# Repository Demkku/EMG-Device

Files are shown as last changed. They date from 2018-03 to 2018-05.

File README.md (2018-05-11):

Everything done, everything up to date and project presented.

final presentation:
https://docs.google.com/presentation/d/1xxOuLbYDE3mbfAP0H2NyMZXC_jU_autwXX0Ozza_mss/edit?usp=sharing

repository:
https://github.com/Demkku/EMG-Device

diary:
https://demkku.github.io/EMG-Device/

## Summary report

click [here]({{ site.baseurl }}/assets/EMG summary report.pdf) to download the summary report PDF with pictures and links
Note! link only available when browsing github pages and the link doesn't seem to work with Edge Browser

Our final concept was to measure heart rate using voltage sensors that have been amplified and filtered using operational amplifiers. Then the heart rate peak is detected with Arduino and the time difference between the peaks is measured and converted for a servo. Then the servo moves a needle on a measuring table to display the heart rate.

Our project consists of 4 elements: a circuit board and a case for it, a measuring table and software to read sensor data and convert into readable data and software to control a servo for the measuring table. 

Johannes designed the circuit board using KiCad. Voltage -sensors didn’t have strong enough signal, so in order to use it properly the signal had to be amplified and filtered using operational amplifiers. The voltage difference in the order of 1mV is measured across the chest with EKG electrodes, +, - and ground. The signal to an instrumental operational amplifier, where common mode noise is rejected, and the signal is amplified. Next, the signal goes through low and high pass filters. After filtering is further amplification and full wave rectification. Last, one more amplifier and then the signal goes to the ADC of ATMEGA328p. 

The case was designed by using Blender. Blender isn’t quite the best software in designing real life objects, but to create a simple and aesthetically nice case wasn’t a problem. The case was designed around the project images exported from Kicad. Some approximation by eye had to be made with components and they were pretty much correct. Only the size of the PCB would have gone terribly wrong if only the Kicad images were followed. The case was finally printed with Fortus 380mc printer. The result was fair, only the bottom was so thin that it cracked a little.

The measuring table was designed with Blender, from which the vector file was imported to Inkscape.
From Inkscape the vector file was exported as a pdf and then printed using a laser cutter out of plywood. The first cut table was too thick, and the servo couldn’t be put through. The arrow needed a hole for the screw, too. That’s why the table was cut again, and it turned out without problems. The servo was glued on the backside of the table.

The software was done on Arduino IDE platform. We programmed our code to ATMEGA328p microcontroller using Arduino UNO. The programs purpose was to measure the time difference between every heartbeat and calculate how many times the heart beats in a minute. EKG -sensors had a triangle wave that measured voltage of the heartbeat and it had some noise in it. To get reliable data we had to calculate the time difference between every peak of the voltage signal and not take the noise into account. We made the program to measure only the rising side of the wave and its maximum voltage. That way we got the most reliable data. Then we had to program a correct angle to a servo to display the heartrate on a measuring table.

Lessons learned 

We learned a lot in this project. We learned to use different software like KiCad, Blender, GitHub and Inkscape. We learned that one should always make a second version of the hardware design if any problems would rise. We learned how to use operational amplifiers in practice and how to compare different components to get the best one for its use. We also learned to watch carefully that everything gets correctly imported other software like all of our parts in the circuit board design didn’t get correctly imported to the drilling machine because we used KiCad as our design system.

We learned a good lesson in time management. It would be a lot better to divide the work of the project to entire period so there wouldn’t be such a rush at the end of the period to get everything done.

Our recommendation to others doing the same project is to take your time designing every element of the project carefully so everything goes smoothly when you start building up the project. This project can be a bit difficult so it would be better done in your on pace and not in an introductory course like Principles of digital fabrication.

Feedback to course responsibles

 The course was nice. It was good change for our usual courses that are heavily theoretic besed. It helped us to learn new things to designour projects so the course was also quite usefull.

## W19

On monday the case is printed, also
project software created and completed as it is very simple. 
The case slightly cracked during removal from the printer.

With the completetion of SW with Aruino IDE and receiving of the mesuring electrodes on the last minute
PROJECT COMPLETED!!!

the complete project:
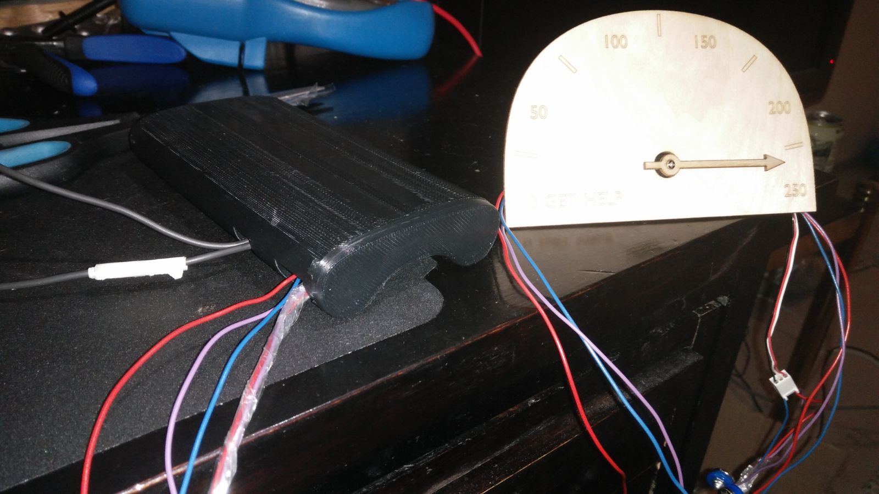
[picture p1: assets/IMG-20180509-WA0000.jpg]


testing after pads finally received:
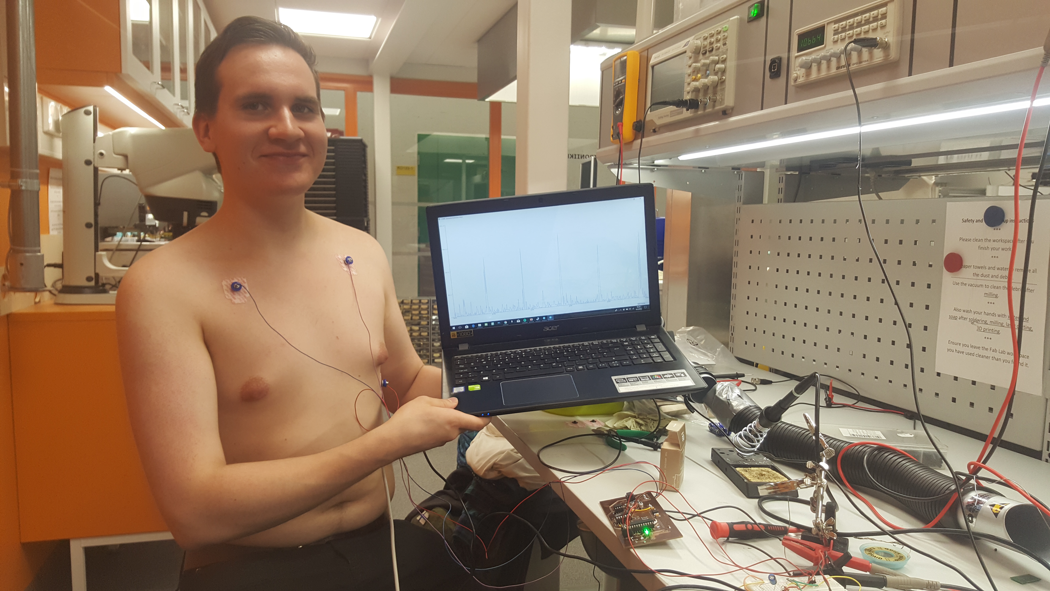
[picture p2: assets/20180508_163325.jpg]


The code:
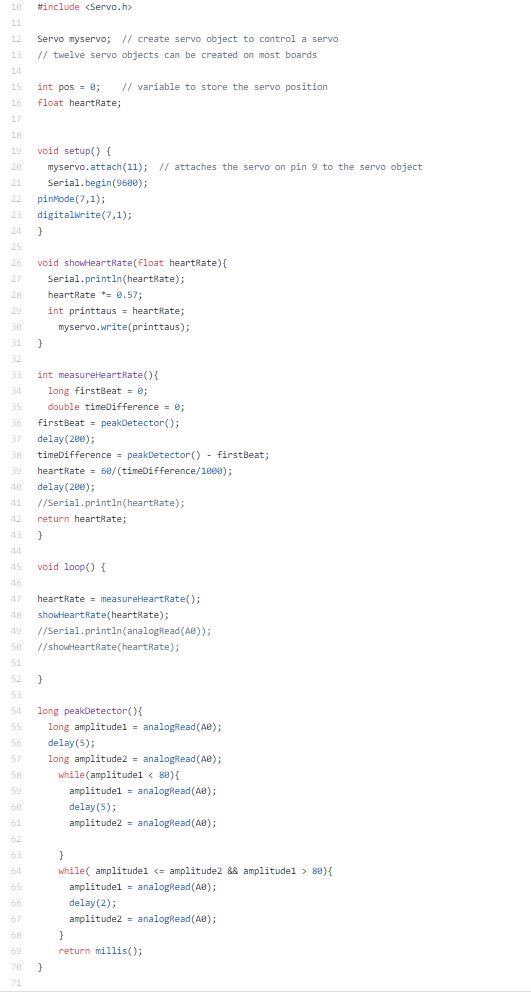
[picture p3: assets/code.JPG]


## W18

Testing software created. Extensive testing and simulation done. 
See baseband testing report and oscilloscope pictures.

final output to ADC on simulation, massive hf noise:
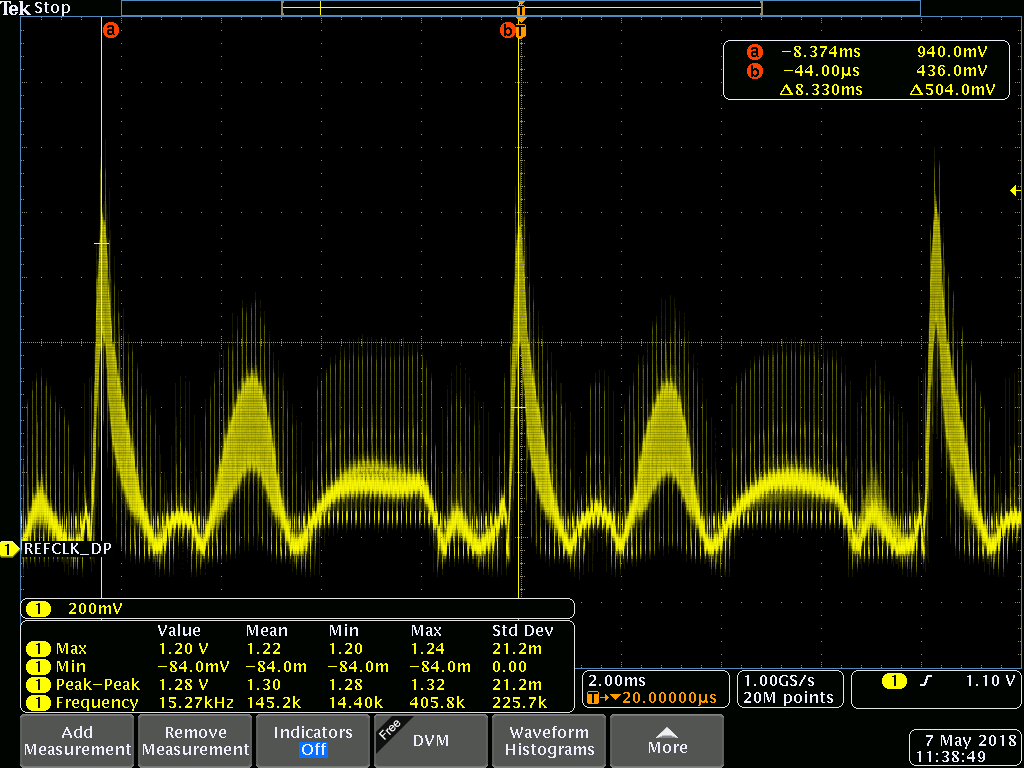
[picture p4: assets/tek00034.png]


Component values changed and filtering added

## W17

The remaining components soldered and measurements taken to the case.
During the soldering, some missing traces noticed, but fixed with jump wires.
Traces missing on the layout.



EKG electrodes ordered from Medkit.

Modeling of the case started with blender.
Also, modeling of the measuring table started with blender.

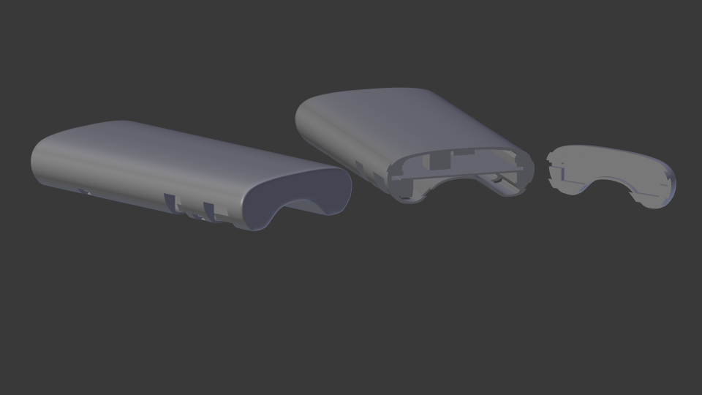
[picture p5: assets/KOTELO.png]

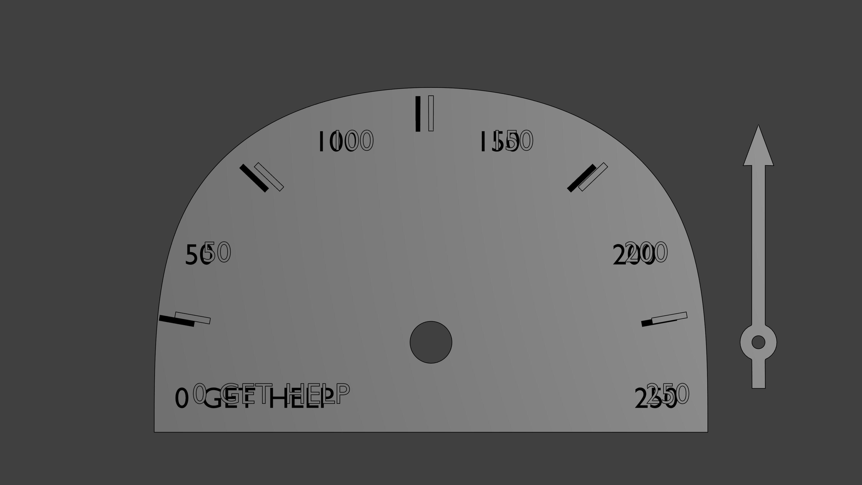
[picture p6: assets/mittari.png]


## W16

Midterm meeting

Later on the week, components received and first soldered.

## W15

The idea maybe changed to a heart rate sensor, which can be measured with the same circuit. 
Will be tested when components received, probably on W16 or 17

V2 board Milled with Success!!!

On the left first try, on the right the V2 board


Components ordered from Mouser.

Design for an enclosure started, will be 3D printed.

## W14

Layout V1 started and completed:
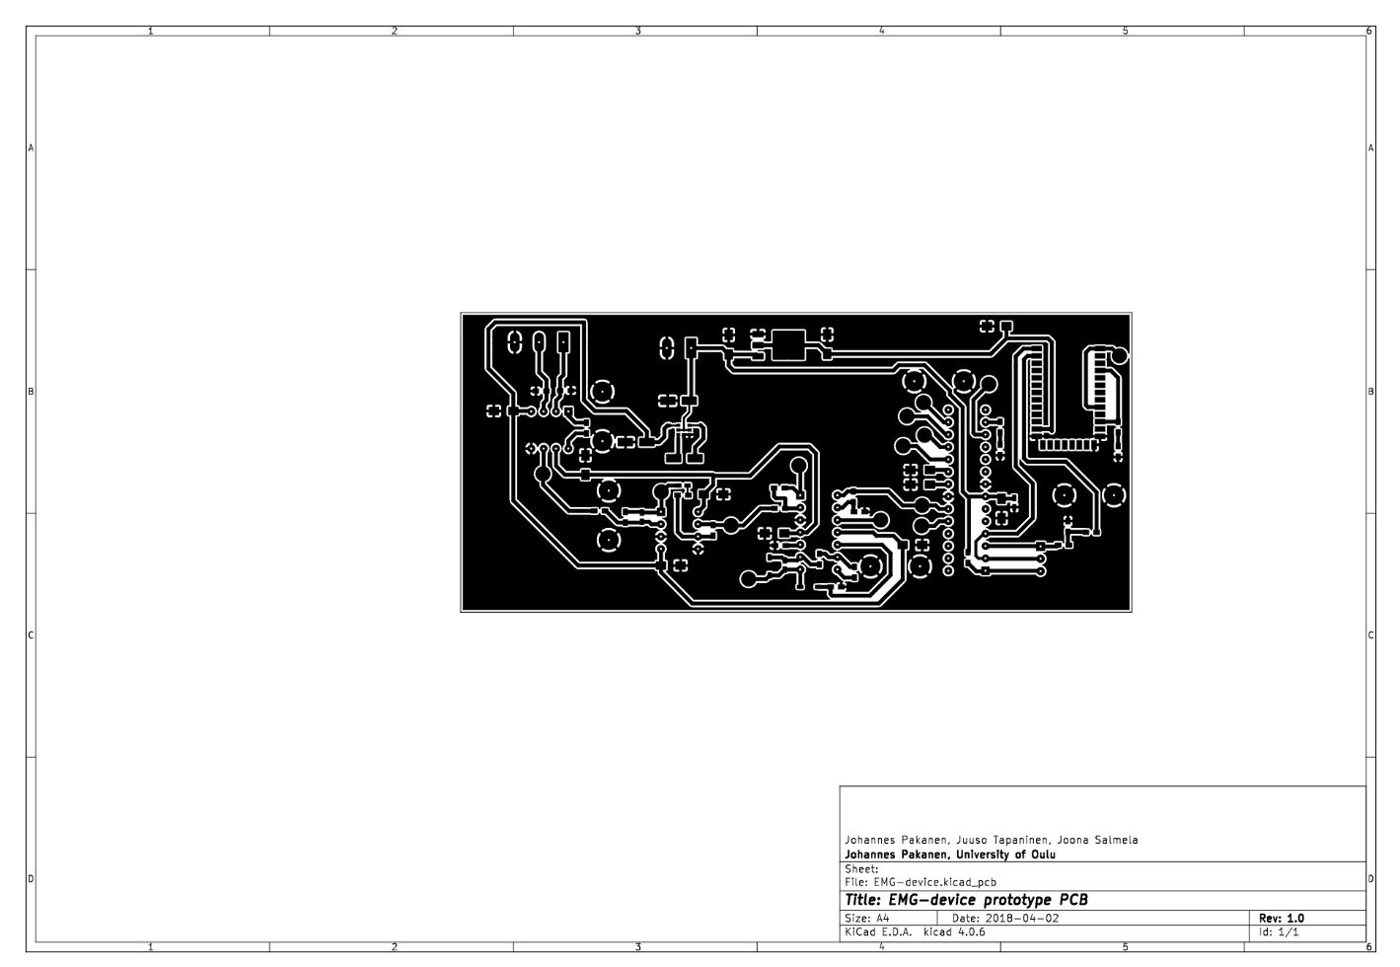
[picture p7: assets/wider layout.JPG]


BOM completed.

V1 board milled. The board failed with board width at 0.4mm and uneven board at milling machine.
As a result wire width doubled to 0.8mm wherever possible.

## W13

After brainstorming requrements set

Kicad schematics started:
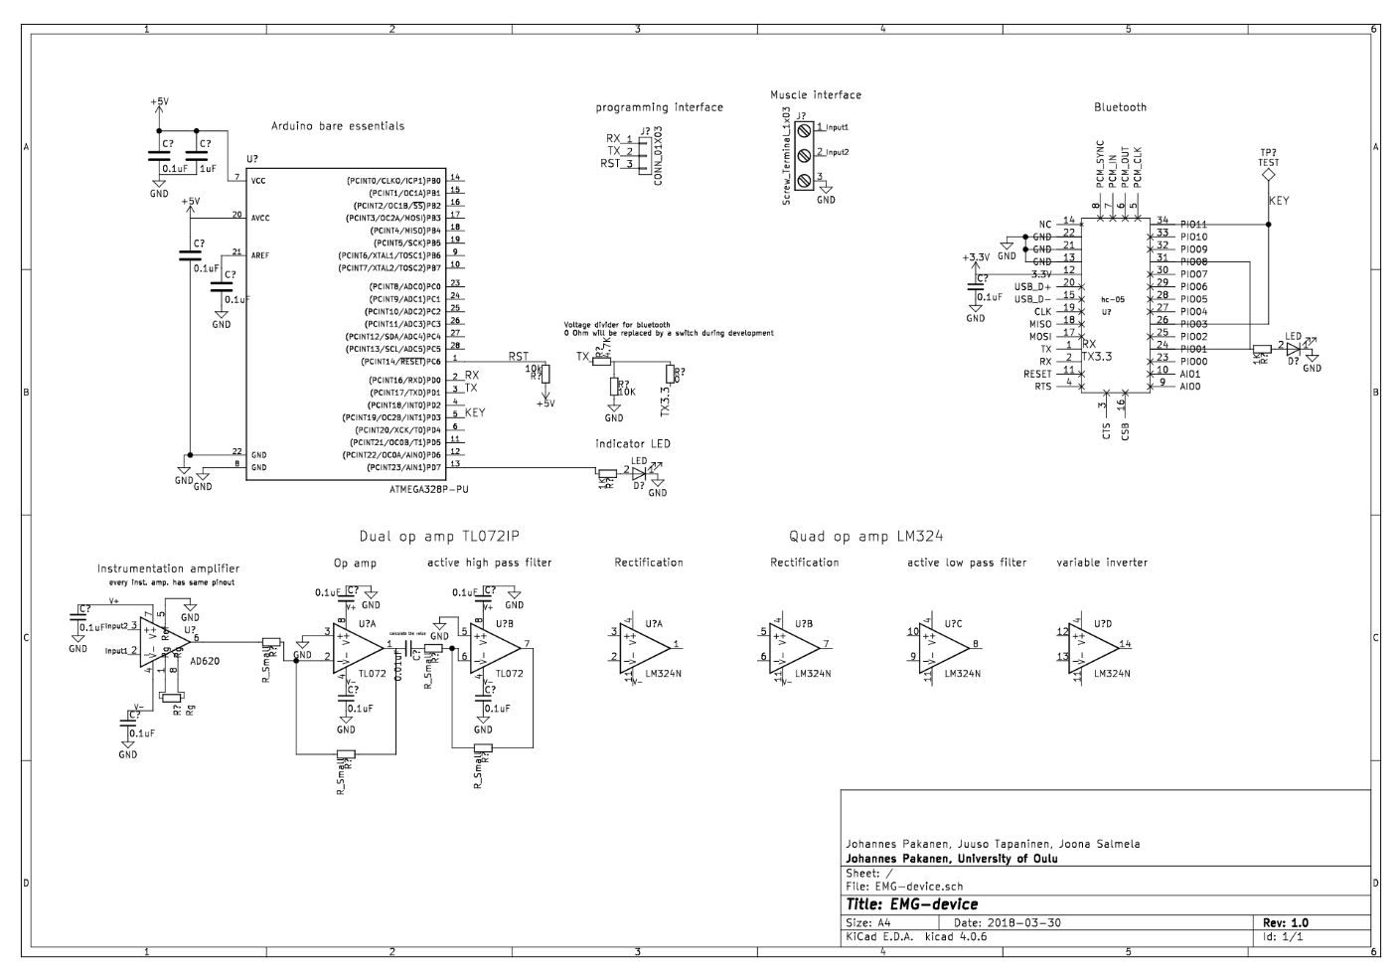
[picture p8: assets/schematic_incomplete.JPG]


Kicad schematics done after a lot of reading about op amps:
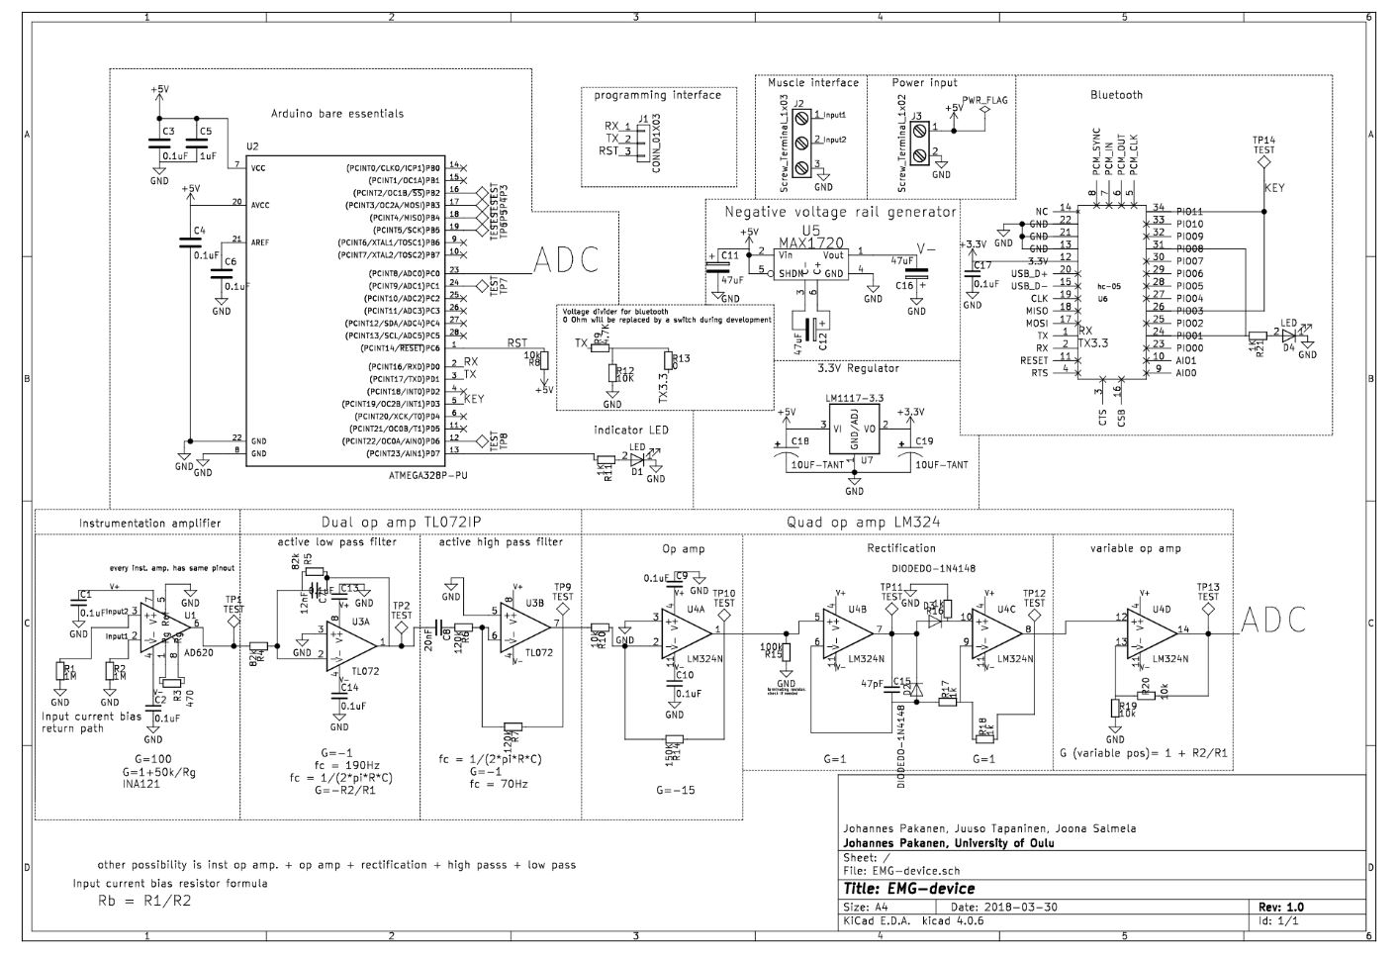
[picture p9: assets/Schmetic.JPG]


## W12

The repositery and site created

## Start of the project:

Introductory report, EMG-Device

521159P Principles of Digital Fabrication 
DIGIFAB10 

The idea is to build a device that can measure EMG signal. EMG signals are created when muscles are used, and nerve impulses are sent. Impulses create a potential difference in the order of 1-10mV which is amplified, filtered and read with an Arduino. To meet course requirements an enclosure will be 3D printed and something laser cut. We arrived at the idea of an EMG device as a combination interest to the subject of bio signals, the challenge and courses about op amps are running in parallel with this course, so we can use in practice what we have learned. 

Other project that we thought of was an Arduino tank that could locate WIFI signal sources, but this would have been very software heavy, and because we are EE students, we wanted to put emphasis on hardware. Also locating sources turns out to be very hard. Our back up plan is an EKG device, which instead of 3 measuring lanes, uses only one.

BOM:
QTY	Component type	Package	Source	Price(eur)	URL

10	0.1uF capacitor	1206	Electronics club	0	

1	1uF capacitor	0603	Johannes	0	

1	12nF capacitor	0603	Johannes	0	

1	20nF capacitor	0603	Johannes	0	

3	47uF capacitor	5x5mm	Johannes	0	

1	47pF capacitor	0603	Johannes	0	

2	10uF tant. Cap.	1206?	Electronics club	0	

2	SMD LED	0603	Johannes	0	

2	1N4148W-F, SMD diode	SOD-123	Mouser	0,3	https://www.mouser.fi/ProductDetail/Diodes-Incorporated/1N4148W-7-F?qs=sGAEpiMZZMvilazpv%252bFqvbevgE8TPEOt

1	3 pin header	male 100mil header	Electronics club	0	

1	3 screw terminal	5mm terminal	Johannes	0	

1	2 screw terminal	5mm terminal	Johannes	0	

2	1MOhm resistor	0603?	Electronics club/Johannes	0	

1	470 Ohm resistor	0603	Johannes	0	

2	82kOhm resistor	0603	Johannes	0	

2	120kOhm resistor	0603	Johannes	0	

5	10kOhm resistor	0603	Johannes	0	

1	4,7kOhm resistor	0603	Johannes	0	

5	1kOhm resistor	0603	Johannes	0	

1	0 Ohm resistor	0603	Johannes	0	

1	15kOhm resistor	0603	Johannes	0	

1	100kOhm resistor	0603	Johannes	0	

2	DIP8 socket	DIP8	Johannes	0	

1	DIP14 socket	DIP14	Johannes	0	

1	DIP28 socket	DIP28	Johannes	0	

1	MAX1720 charge pump	TSOP-6	Mouser	0,58	https://www.mouser.fi/ProductDetail/ON-Semiconductor/MAX1720EUTG?qs=sGAEpiMZZMtitjHzVIkrqdfdkrf0Qy0Qzg%252b1DRXikVE%3d

1	HC-05 BT unit	custom	Johannes	0	

1	INA121PA inst. amp.	DIP8	Mouser	4,94	https://www.mouser.fi/ProductDetail/Texas-Instruments/INA121PA?qs=sGAEpiMZZMsE1dKaA2ImUPh%2fgv48%2feoeALcGDSe487k%3d

1	TL072IP op. Amp.	DIP8	Mouser	0,56	https://www.mouser.fi/ProductDetail/Texas-Instruments/TL072IP?qs=5BZzbFV4k2v7IBrcArRPQw==

1	LM324N	DIP14	Mouser	0,43	https://www.mouser.fi/ProductDetail/Texas-Instruments/LM324N?qs=sGAEpiMZZMtCHixnSjNA6Araa3jp4DVB37ZJv3RooEc%3d

1	ATMega 328p	DIP28	Electronics club	0	

1	LM1117 3.3V regulator	TO252	Electronics club	0	

8	button things	button	Johannes	0	

50	Electrodes, 34mm	button	Medkit.fi	14,26	https://www.medkit.fi/ambu-blue-sensor-m-oo-s?___store=finland&nosto=frontpage-nosto-1

## Welcome to GitHub Pages

You can use the [editor on GitHub](https://github.com/Demkku/EMG-Device/edit/master/README.md) to maintain and preview the content for your website in Markdown files.

Whenever you commit to this repository, GitHub Pages will run [Jekyll](https://jekyllrb.com/) to rebuild the pages in your site, from the content in your Markdown files.

### Markdown

Markdown is a lightweight and easy-to-use syntax for styling your writing. It includes conventions for

```markdown
Syntax highlighted code block

# Header 1
## Header 2
### Header 3

- Bulleted
- List

1. Numbered
2. List

**Bold** and _Italic_ and `Code` text

[Link](url) and ![Image](src)
```

For more details see [GitHub Flavored Markdown](https://guides.github.com/features/mastering-markdown/).

### Jekyll Themes

Your Pages site will use the layout and styles from the Jekyll theme you have selected in your [repository settings](https://github.com/Demkku/EMG-Device/settings). The name of this theme is saved in the Jekyll `_config.yml` configuration file.

### Support or Contact

Having trouble with Pages? Check out our [documentation](https://help.github.com/categories/github-pages-basics/) or [contact support](https://github.com/contact) and we’ll help you sort it out.

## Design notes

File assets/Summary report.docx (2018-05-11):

Summary report

Our final concept was to measure heart rate using voltage sensors that have been amplified and filtered using operational amplifiers. Then the heart rate peak is detected with Arduino and the time difference between the peaks is measured and converted for a servo. Then the servo moves a needle on a measuring table to display the heart rate.

Our project consists of 4 elements: a circuit board and a case for it, a measuring table and software to read sensor data and convert into readable data and software to control a servo for the measuring table.

Johannes designed the circuit board using KiCad. Voltage -sensors didn’t have strong enough signal, so to use it properly the signal had to be amplified and filtered using operational amplifiers. The voltage difference in the order of 1mV is measured across the chest with EKG electrodes, +, - and ground. The signal to an instrumental operational amplifier, where common mode noise is rejected, and the signal is amplified. Next, the signal goes through low and high pass filters. After filtering is further amplification and full wave rectification. Last, one more amplifier and then the signal goes to the ADC of ATMEGA328p.

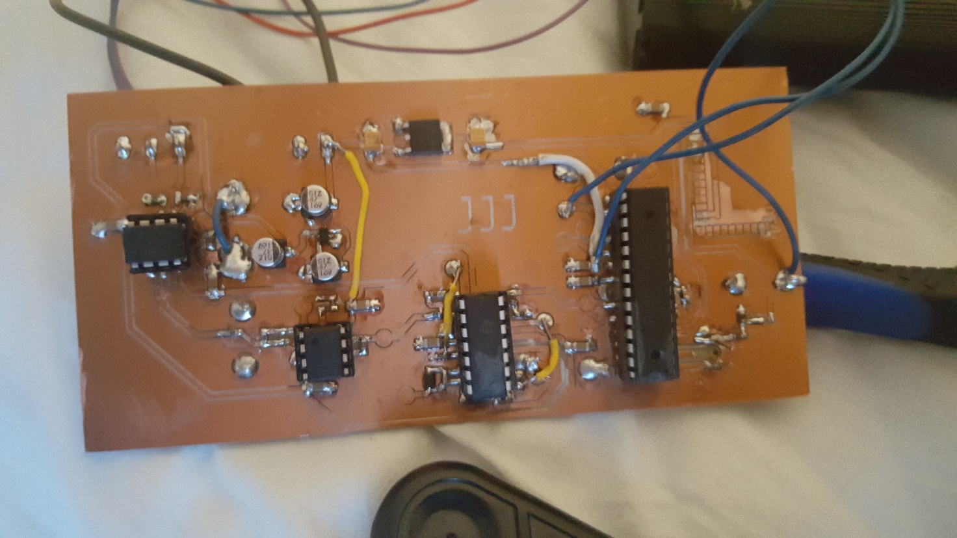
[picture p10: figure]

The complete board

The case was designed by using Blender. Blender isn’t quite the best software in designing real life objects, but to create a simple and aesthetically nice case wasn’t a problem. The case was designed around the project images exported from Kicad. Some approximation by eye had to be made with components and they were pretty much correct. Only the size of the PCB would have gone terribly wrong if only the Kicad images were followed. The case was finally printed with Fortus 380mc printer. The result was fair, only the bottom was so thin that it cracked a little.


The measuring table was designed with Blender, from which the vector file was imported to Inkscape.

From Inkscape the vector file was exported as a pdf and then printed using a laser cutter out of plywood. The first cut table was too thick, and the servo couldn’t be put through. The arrow needed a hole for the screw, too. That’s why the table was cut again, and it turned out without problems. The servo was glued on the backside of the table.

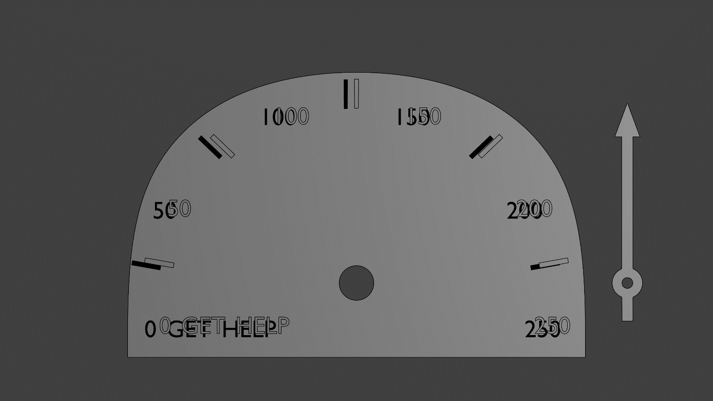
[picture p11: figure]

The software was done on Arduino IDE platform. We programmed our code to ATMEGA328p microcontroller using Arduino UNO. The programs purpose was to measure the time difference between every heartbeat and calculate how many times the heart beats in a minute. EKG -sensors had a triangle wave that measured voltage of the heartbeat and it had some noise in it. To get reliable data we had to calculate the time difference between every peak of the voltage signal and not take the noise into account. We made the program to measure only the rising side of the wave and its maximum voltage. That way we got the most reliable data. Then we had to program a correct angle to a servo to display the heartrate on a measuring table.

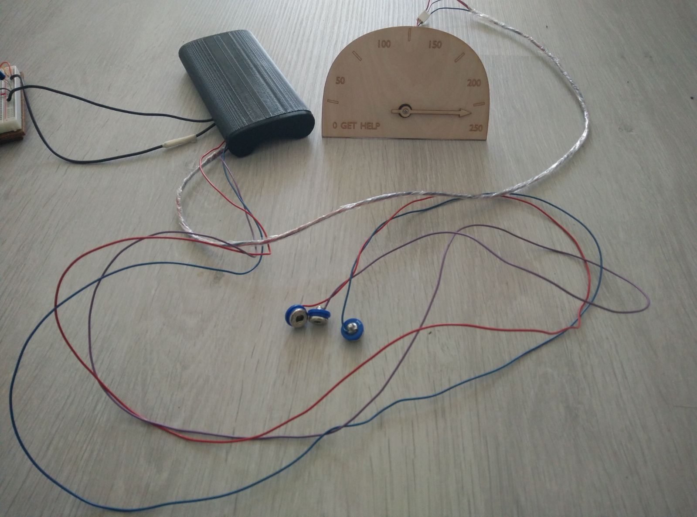
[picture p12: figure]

Finished project

Lessons learned

We learned a lot in this project. We learned to use different software like KiCad, Blender, GitHub and Inkscape. We learned that one should always make a second version of the hardware design if any problems would rise. We learned how to use operational amplifiers in practice and how to compare different components to get the best one for its use. We also learned to watch carefully that everything gets correctly imported other software like all our parts in the circuit board design didn’t get correctly imported to the drilling machine because we used KiCad as our design system.

We learned a good lesson in time management. It would be a lot better to divide the work of the project to entire period so there wouldn’t be such a rush at the end of the period to get everything done.

Our recommendation to others doing the same project is to take your time designing every element of the project carefully so everything goes smoothly when you start building up the project. This project can be a bit difficult, so it would be better done in your on pace and not in an introductory course like Principles of digital fabrication.

Feedback to course responsible

The course was nice. It was good change for our usual courses that are heavily theoretic based. It helped us to learn new things to design our projects, so the course was also quite useful.

final presentation:

https://docs.google.com/presentation/d/1xxOuLbYDE3mbfAP0H2NyMZXC_jU_autwXX0Ozza_mss/edit?usp=sharing

repository:

https://github.com/Demkku/EMG-Device

diary:

https://demkku.github.io/EMG-Device/

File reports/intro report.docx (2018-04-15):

# Introductory report, EMG-Device

# 521159P Principles of Digital Fabrication (https://wiki.oulu.fi/display/DIGIFAB/521159P+Principles+of+Digital+Fabrication+Home)

DIGIFAB10

The idea is to build a device that can measure EMG signal. EMG signals are created when muscles are used, and nerve impulses are sent. Impulses create a potential difference in the order of 1-10mV which is amplified, filtered and read with an Arduino. To meet course requirements an enclosure will be 3D printed and something laser cut. We arrived at the idea of an EMG device as a combination interest to the subject of bio signals, the challenge and courses about op amps are running in parallel with this course, so we can use in practice what we have learned.

Other project that we thought of was an Arduino tank that could locate WIFI signal sources, but this would have been very software heavy, and because we are EE students, we wanted to put emphasis on hardware. Also locating sources turns out to be very hard. Our back up plan is an EKG device, which instead of 3 measuring lanes, uses only one.

BOM:

QTY | Component type | Package | Source | Price(eur) | URL
10 | 0.1uF capacitor | 1206 | Electronics club | 0
1 | 1uF capacitor | 0603 | Johannes | 0
1 | 12nF capacitor | 0603 | Johannes | 0
1 | 20nF capacitor | 0603 | Johannes | 0
3 | 47uF capacitor | 5x5mm | Johannes | 0
1 | 47pF capacitor | 0603 | Johannes | 0
2 | 10uF tant. Cap. | 1206? | Electronics club | 0
2 | SMD LED | 0603 | Johannes | 0
2 | 1N4148W-F, SMD diode | SOD-123 | Mouser | 0,3 | https://www.mouser.fi/ProductDetail/Diodes-Incorporated/1N4148W-7-F?qs=sGAEpiMZZMvilazpv%252bFqvbevgE8TPEOt
1 | 3 pin header | male 100mil header | Electronics club | 0
1 | 3 screw terminal | 5mm terminal | Johannes | 0
1 | 2 screw terminal | 5mm terminal | Johannes | 0
2 | 1MOhm resistor | 0603? | Electronics club/Johannes | 0
1 | 470 Ohm resistor | 0603 | Johannes | 0
2 | 82kOhm resistor | 0603 | Johannes | 0
2 | 120kOhm resistor | 0603 | Johannes | 0
5 | 10kOhm resistor | 0603 | Johannes | 0
1 | 4,7kOhm resistor | 0603 | Johannes | 0
5 | 1kOhm resistor | 0603 | Johannes | 0
1 | 0 Ohm resistor | 0603 | Johannes | 0
1 | 15kOhm resistor | 0603 | Johannes | 0
1 | 100kOhm resistor | 0603 | Johannes | 0
2 | DIP8 socket | DIP8 | Johannes | 0
1 | DIP14 socket | DIP14 | Johannes | 0
1 | DIP28 socket | DIP28 | Johannes | 0
1 | MAX1720 charge pump | TSOP-6 | Mouser | 0,58 | https://www.mouser.fi/ProductDetail/ON-Semiconductor/MAX1720EUTG?qs=sGAEpiMZZMtitjHzVIkrqdfdkrf0Qy0Qzg%252b1DRXikVE%3d
1 | HC-05 BT unit | custom | Johannes | 0
1 | INA121PA inst. amp. | DIP8 | Mouser | 4,94 | https://www.mouser.fi/ProductDetail/Texas-Instruments/INA121PA?qs=sGAEpiMZZMsE1dKaA2ImUPh%2fgv48%2feoeALcGDSe487k%3d
1 | TL072IP op. Amp. | DIP8 | Mouser | 0,56 | https://www.mouser.fi/ProductDetail/Texas-Instruments/TL072IP?qs=5BZzbFV4k2v7IBrcArRPQw==
1 | LM324N | DIP14 | Mouser | 0,43 | https://www.mouser.fi/ProductDetail/Texas-Instruments/LM324N?qs=sGAEpiMZZMtCHixnSjNA6Araa3jp4DVB37ZJv3RooEc%3d
1 | ATMega 328p | DIP28 | Electronics club | 0
1 | LM1117 3.3V regulator | TO252 | Electronics club | 0
8 | button things | button | Johannes | 0
50 | Electrodes, 34mm | button | Medkit.fi | 14,26 | https://www.medkit.fi/ambu-blue-sensor-m-oo-s?___store=finland&nosto=frontpage-nosto-1

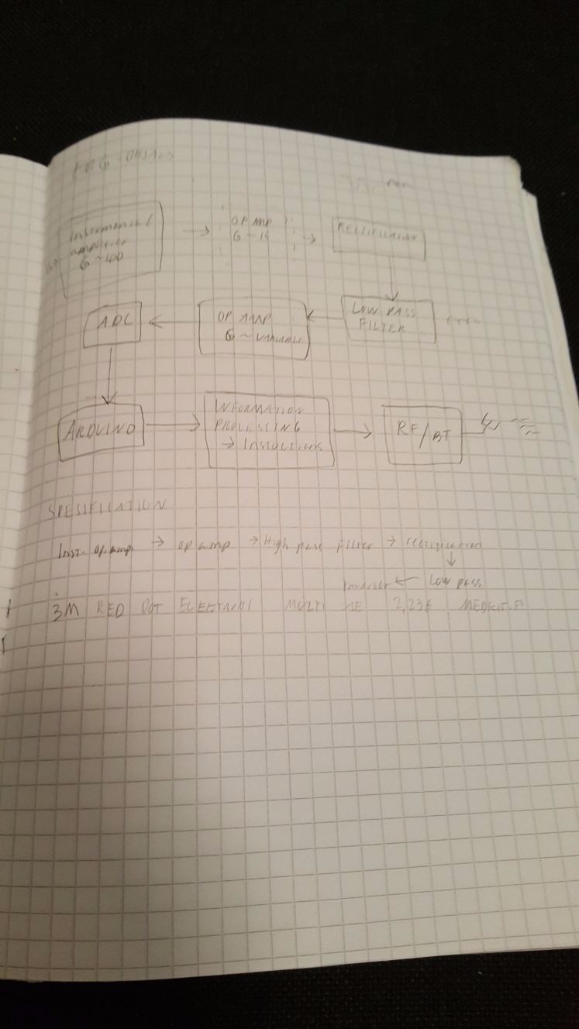
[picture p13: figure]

the original sketch

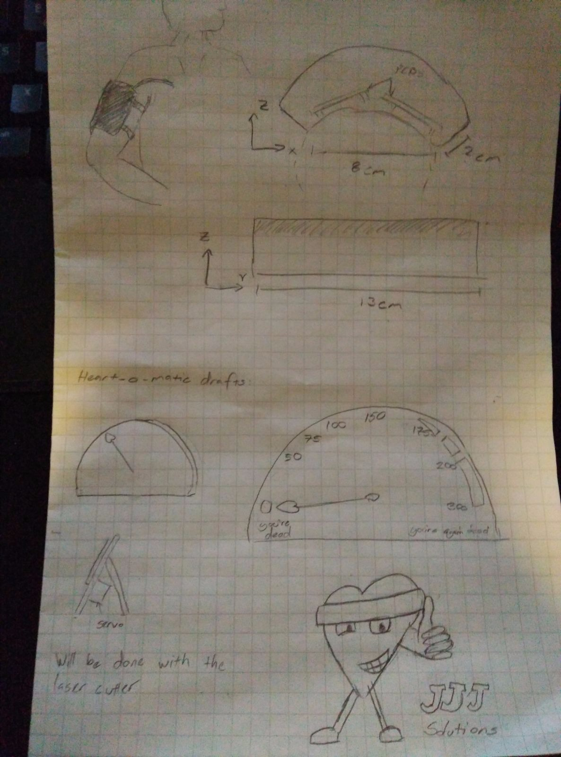
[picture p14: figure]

sketch

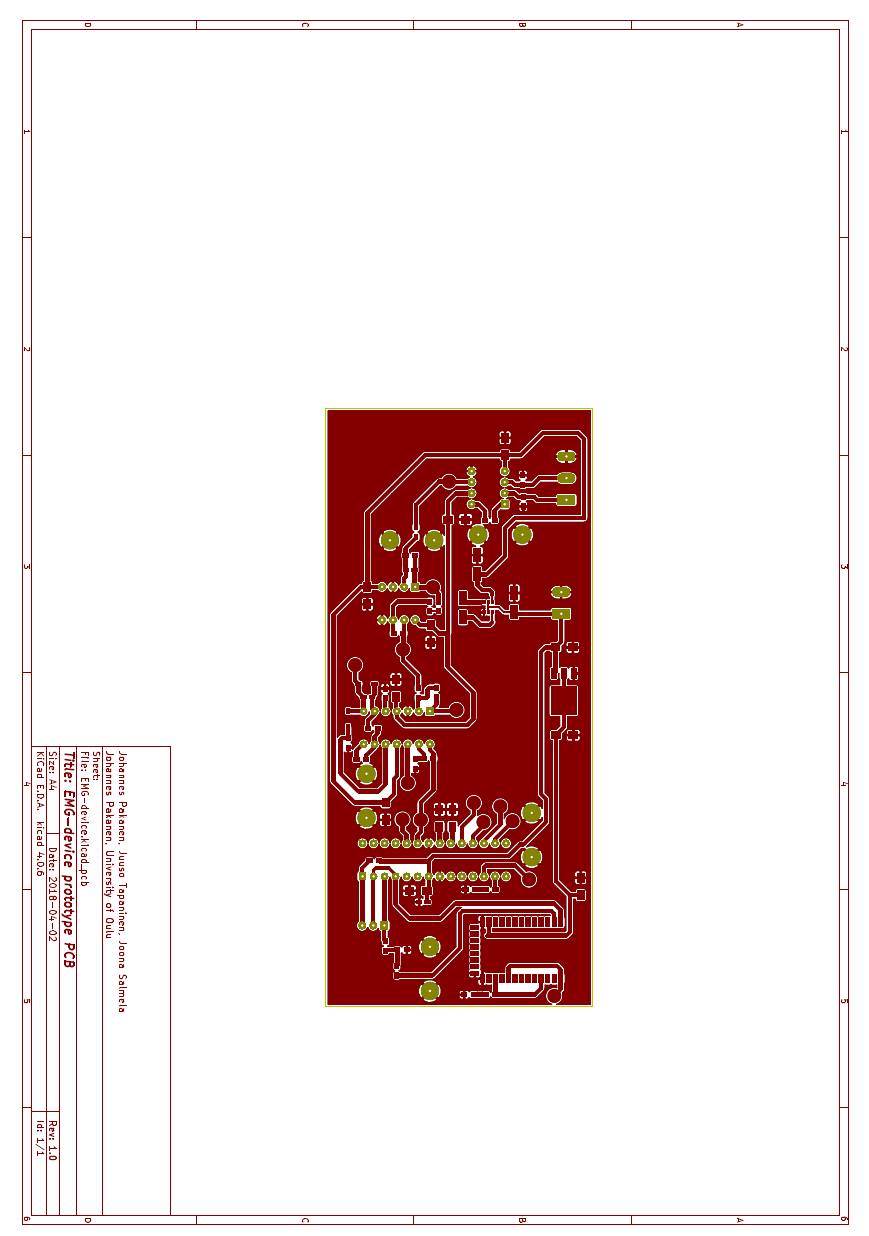
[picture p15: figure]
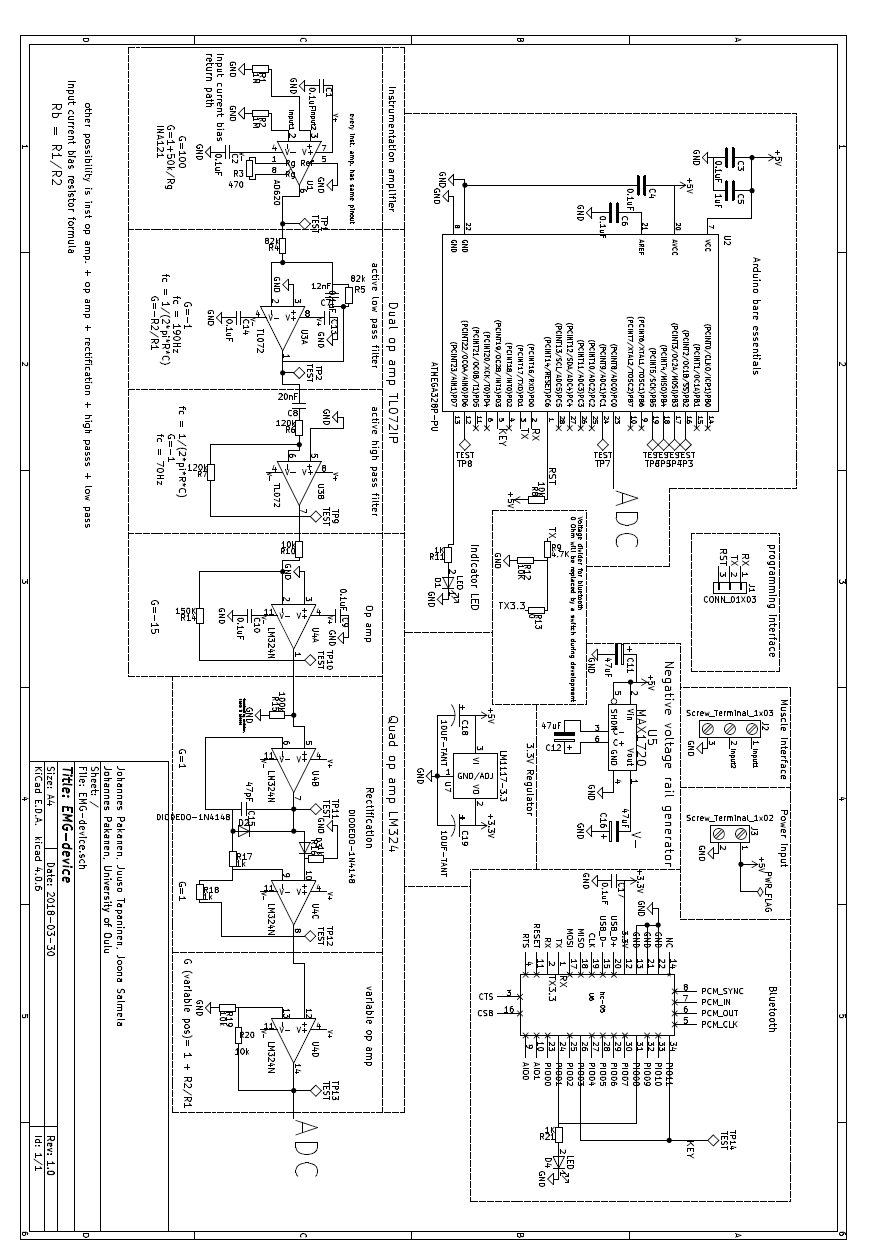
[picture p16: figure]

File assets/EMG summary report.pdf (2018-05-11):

## Summary report

Our final concept was to measure heart rate using voltage sensors that have been amplified and filtered using operational amplifiers. Then the heart rate peak is detected with Arduino and the time difference between the peaks is measured and converted for a servo. Then the servo moves a needle on a measuring table to display the heart rate.
Our project consists of 4 elements: a circuit board and a case for it, a measuring table and software to read sensor data and convert into readable data and software to control a servo for the measuring table. Johannes designed the circuit board using KiCad. Voltage -sensors didn’t have strong enough signal, so to use it properly the signal had to be amplified and filtered using operational amplifiers. The voltage difference in the order of 1mV is measured across the chest with EKG electrodes, +, - and ground. The signal to an instrumental operational amplifier, where common mode noise is rejected, and the signal is amplified. Next, the signal goes through low and high pass filters. After filtering is further amplification and full wave rectification. Last, one more amplifier and then the signal goes to the ADC of ATMEGA328p.

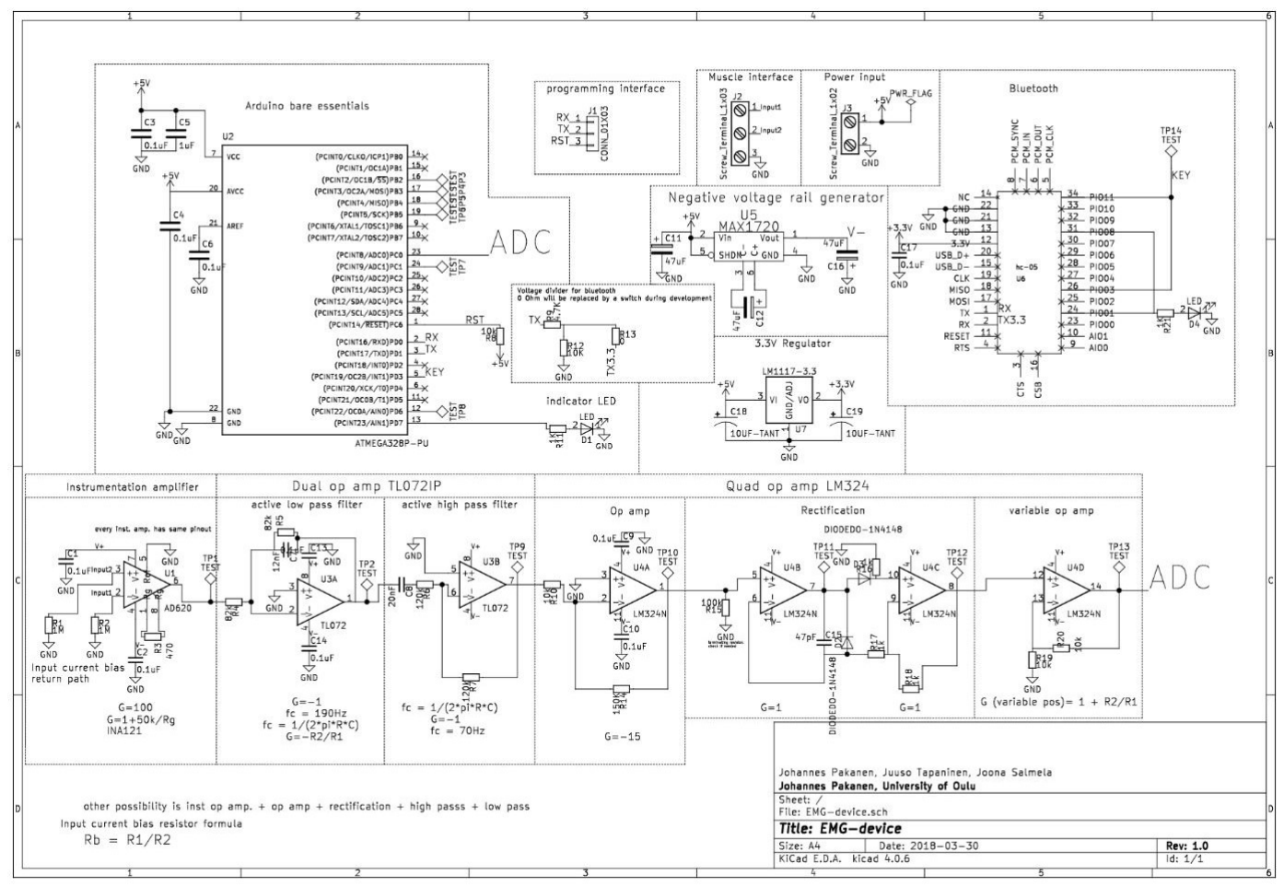
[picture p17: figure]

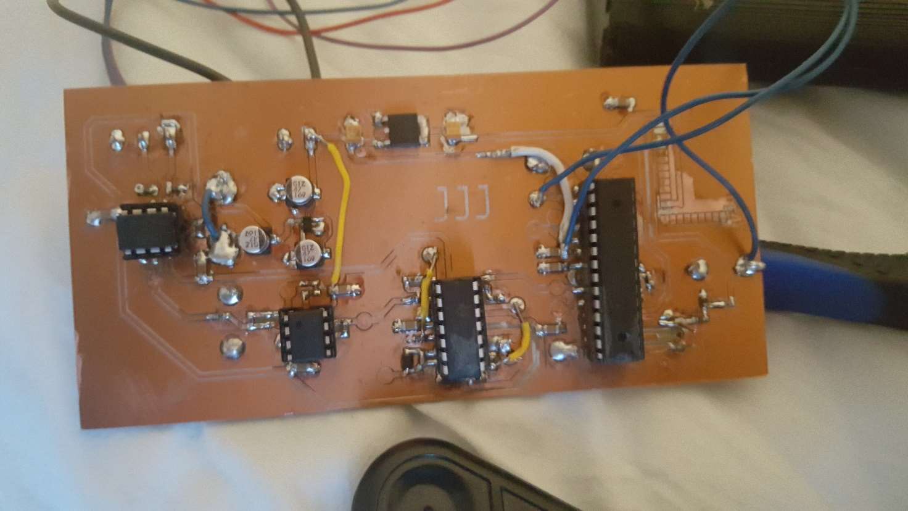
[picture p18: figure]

The complete board

The case was designed by using Blender. Blender isn’t quite the best software in designing real life objects, but to create a simple and aesthetically nice case wasn’t a problem. The case was designed around the project images exported from Kicad. Some approximation by eye had to be made with components and they were pretty much correct. Only the size of the PCB would have gone terribly wrong if only the Kicad images were followed. The case was finally printed with Fortus 380mc printer. The result was fair, only the bottom was so thin that it cracked a little.

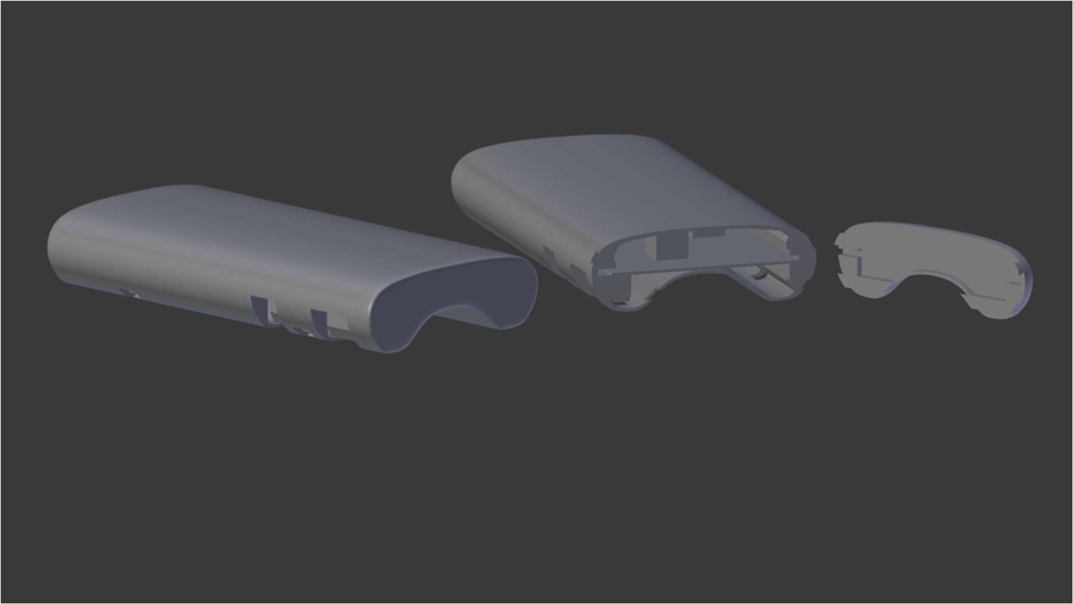
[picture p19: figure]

The measuring table was designed with Blender, from which the vector file was imported to Inkscape. From Inkscape the vector file was exported as a pdf and then printed using a laser cutter out of plywood. The first cut table was too thick, and the servo couldn’t be put through. The arrow needed a hole for the screw, too. That’s why the table was cut again, and it turned out without problems. The servo was glued on the backside of the table.

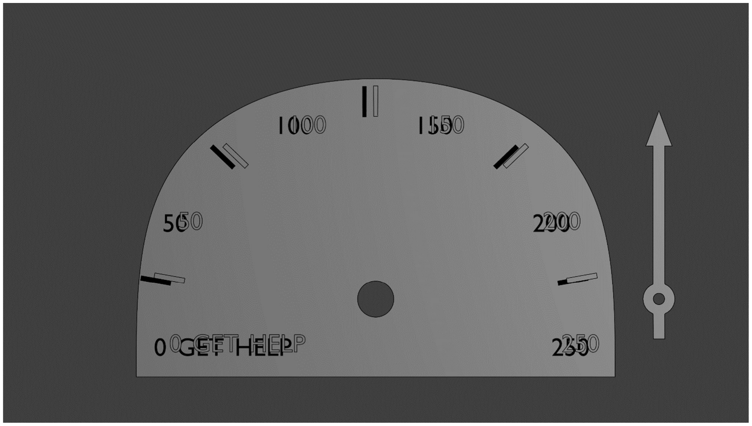
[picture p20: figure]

The software was done on Arduino IDE platform. We programmed our code to ATMEGA328p microcontroller using Arduino UNO. The programs purpose was to measure the time difference between every heartbeat and calculate how many times the heart beats in a minute. EKG -sensors had a triangle wave that measured voltage of the heartbeat and it had some noise in it. To get reliable data we had to calculate the time difference between every peak of the voltage signal and not take the noise into account. We made the program to measure only the rising side of the wave and its maximum voltage. That way we got the most reliable data. Then we had to program a correct angle to a servo to display the heartrate on a measuring table.

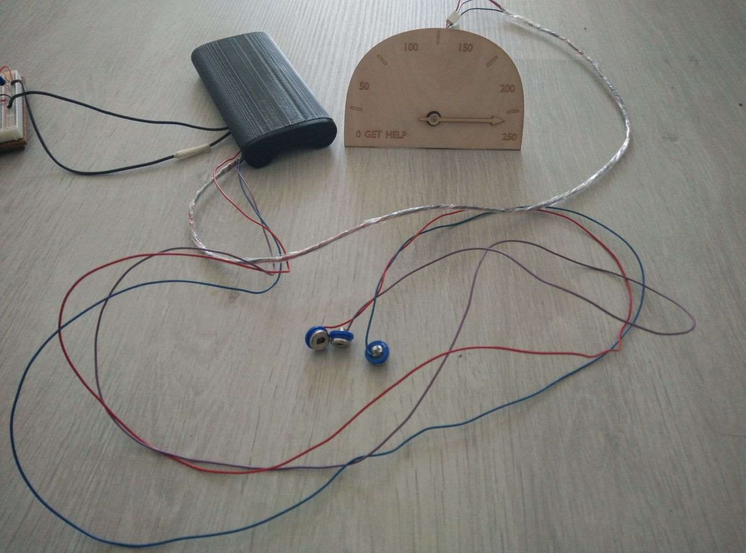
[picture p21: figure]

Finished project

## Lessons learned

We learned a lot in this project. We learned to use different software like KiCad, Blender, GitHub and Inkscape. We learned that one should always make a second version of the hardware design if any problems would rise. We learned how to use operational amplifiers in practice and how to compare different components to get the best one for its use. We also learned to watch carefully that everything gets correctly imported other software like all our parts in the circuit board design didn’t get correctly imported to the drilling machine because we used KiCad as our design system.
We learned a good lesson in time management. It would be a lot better to divide the work of the project to entire period so there wouldn’t be such a rush at the end of the period to get everything done.
Our recommendation to others doing the same project is to take your time designing every element of the project carefully so everything goes smoothly when you start building up the project. This project can be a bit difficult, so it would be better done in your on pace and not in an introductory course like Principles of digital fabrication.

## Feedback to course responsible

The course was nice. It was good change for our usual courses that are heavily theoretic based. It helped us to learn new things to design our projects, so the course was also quite useful.

final presentation:
https://docs.google.com/presentation/d/1xxOuLbYDE3mbfAP0H2NyMZXC_jU_autwXX0Ozza_mss/edit?usp=sharing

repository:
https://github.com/Demkku/EMG-Device

diary:
https://demkku.github.io/EMG-Device/

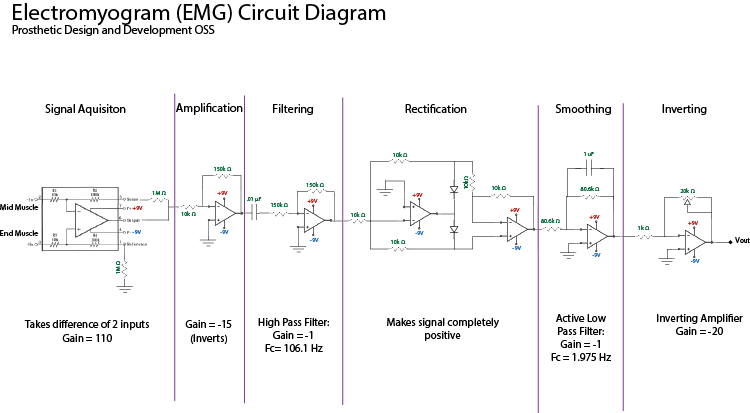
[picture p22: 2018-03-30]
documents/emg-schematic-example.png

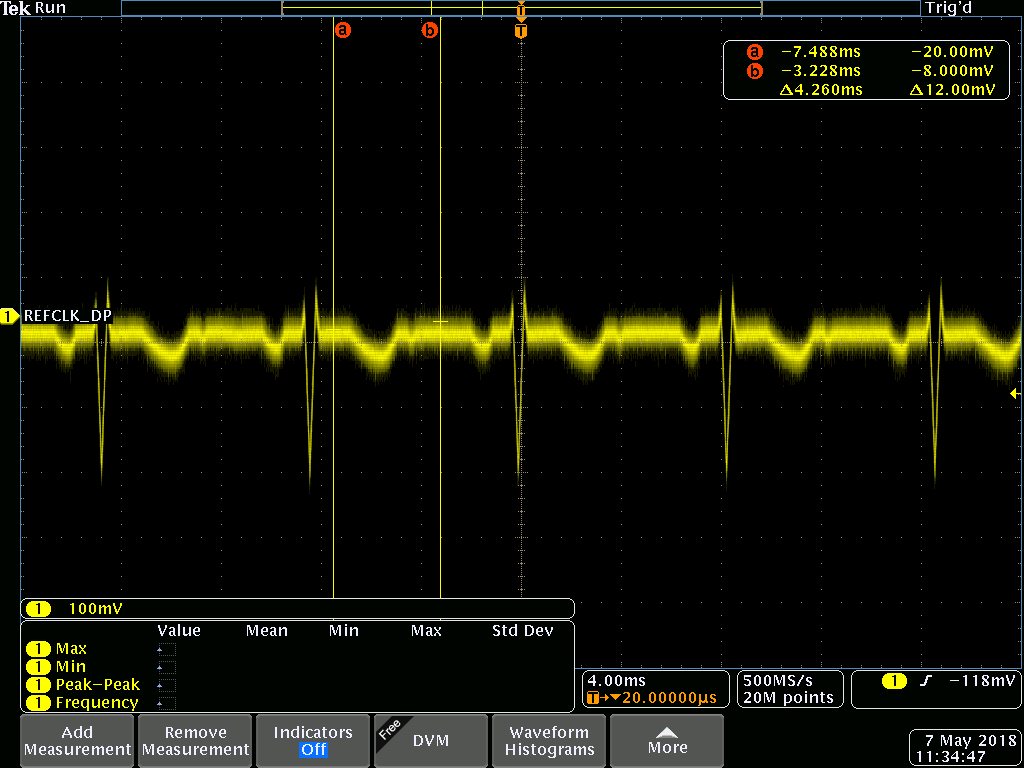
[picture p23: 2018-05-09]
assets/tek00029.png

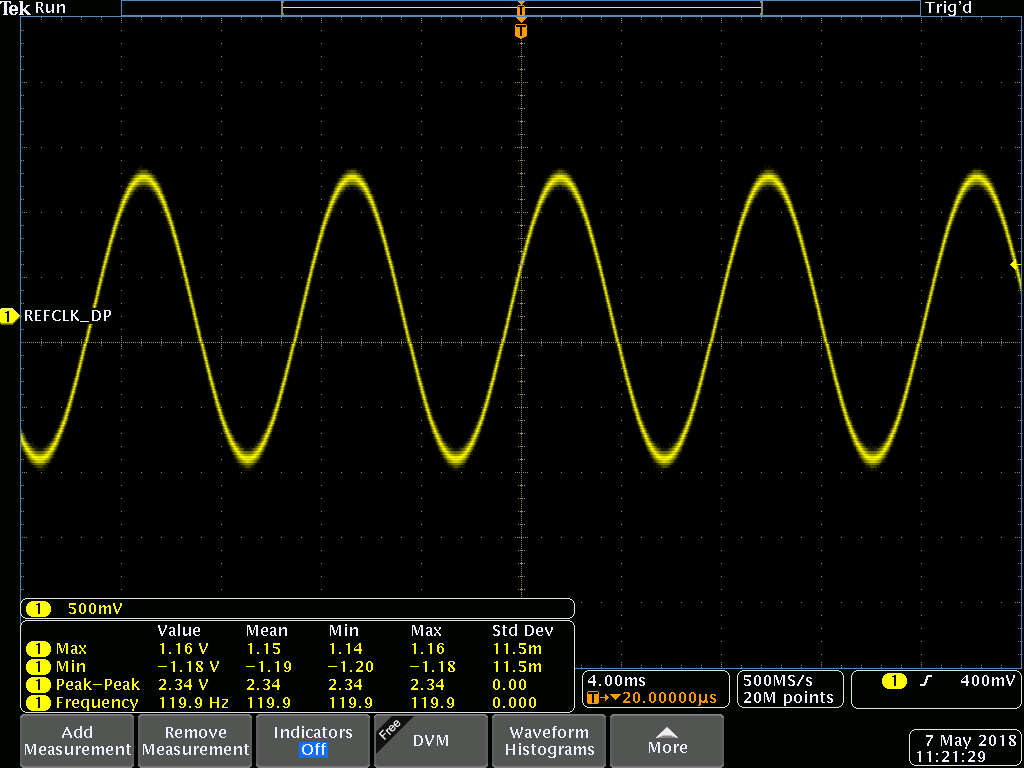
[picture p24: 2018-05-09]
assets/tek00016.png

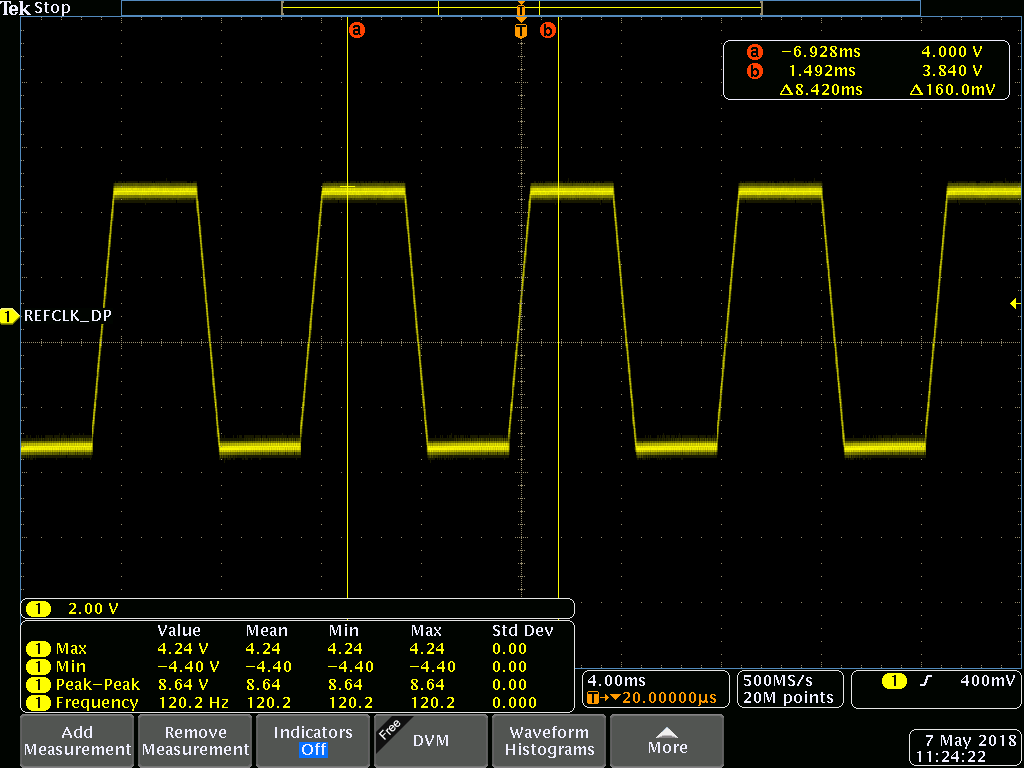
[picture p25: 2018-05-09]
assets/tek00020.png

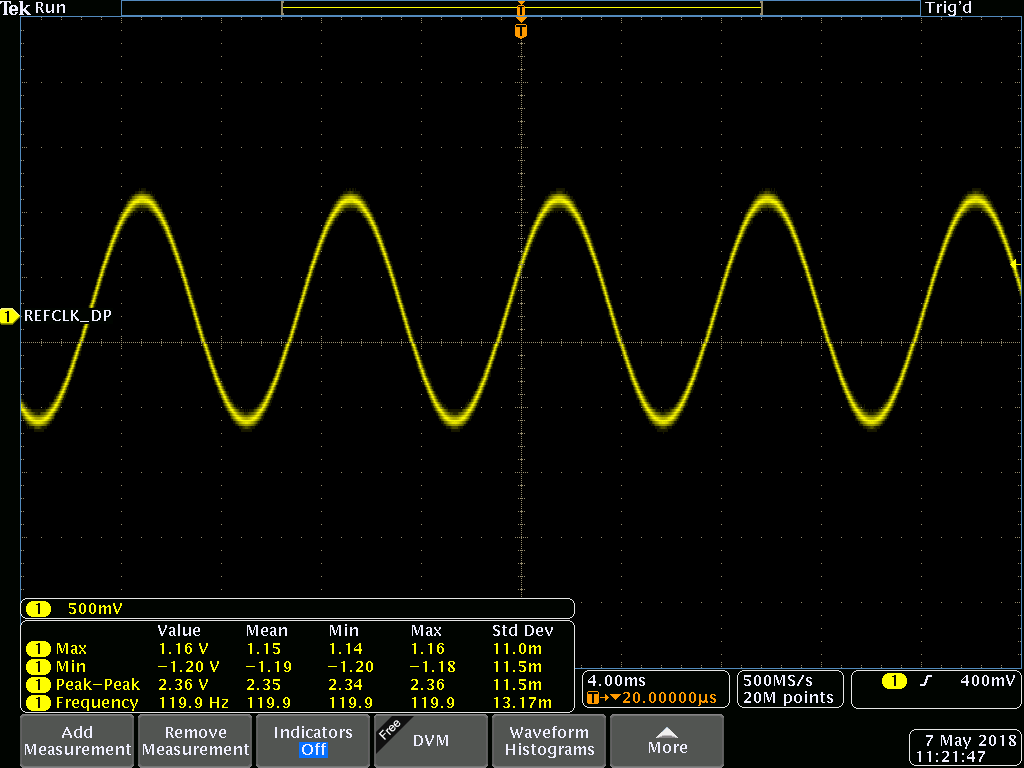
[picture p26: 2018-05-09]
assets/tek00017.png

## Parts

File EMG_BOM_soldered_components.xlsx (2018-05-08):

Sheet: BOM
QTY | Component type | Package | Source | Price(eur) | URL
10 | 0.1uF capacitor | 1206 | Electronics club | 0 |  | x
1 | 1uF capacitor | 0603 | Johannes | 0
1 | 12nF capacitor | 0603 | Johannes | 0
1 | 20nF capacitor | 0603 | Johannes | 0
3 | 47uF capacitor | 5x5mm | Johannes | 0
1 | 47pF capacitor | 0603 | Johannes | 0
2 | 10uF tant. Cap. | 1206? | Electronics club | 0
2 | SMD LED | 0603 | Johannes | 0
2 | 1N4148W-F, SMD diode | SOD-123 | Mouser | 0.3 | https://www.mouser.fi/ProductDetail/Diodes-Incorporated/1N4148W-7-F?qs=sGAEpiMZZMvilazpv%252bFqvbevgE8TPEOt
1 | 3 pin header | male 100mil header | Electronics club | 0
1 | 3 screw terminal | 5mm terminal | Johannes | 0
1 | 2 screw terminal | 5mm terminal | Johannes | 0
2 | 1MOhm resistor | 0603? | Electronics club/Johannes | 0 | x
1 | 470 Ohm resistor | 0603 | Johannes | 0 | x
2 | 82kOhm resistor | 0603 | Johannes | 0 | x
2 | 120kOhm resistor | 0603 | Johannes | 0 | x
5 | 10kOhm resistor | 0603 | Johannes | 0 | x
1 | 4,7kOhm resistor | 0603 | Johannes | 0 | x
5 | 1kOhm resistor | 0603 | Johannes | 0 | x
1 | 0 Ohm resistor | 0603 | Johannes | 0
1 | 15kOhm resistor | 0603 | Johannes | 0 | ?
1 | 100kOhm resistor | 0603 | Johannes | 0 | x
2 | DIP8 socket | DIP8 | Johannes | 0
1 | DIP14 socket | DIP14 | Johannes | 0
1 | DIP28 socket | DIP28 | Johannes | 0
1 | MAX1720 charge pump | TSOP-6 | Mouser | 0.58 | https://www.mouser.fi/ProductDetail/ON-Semiconductor/MAX1720EUTG
1 | HC-05 BT unit | custom | Johannes | 0
1 | INA121PA inst. amp. | DIP8 | Mouser | 4.94 | https://www.mouser.fi/ProductDetail/Texas-Instruments/INA121PA
1 | TL072IP op. Amp. | DIP8 | Mouser | 0.56 | https://www.mouser.fi/ProductDetail/Texas-Instruments/TL072IP?qs=5BZzbFV4k2v7IBrcArRPQw==
1 | LM324N | DIP14 | Mouser | 0.43 | https://www.mouser.fi/ProductDetail/Texas-Instruments/LM324N?qs=sGAEpiMZZMtCHixnSjNA6Araa3jp4DVB37ZJv3RooEc%3d
1 | ATMega 328p | DIP28 | Electronics club | 0
1 | LM1117 3.3V regulator | TO252 | Electronics club | 0
8 | button things | button | Johannes | 0
50 | Electrodes, 34mm | button | Medkit.fi | 14.26 | https://www.medkit.fi/ambu-blue-sensor-m-oo-s?___store=finland&nosto=frontpage-nosto-1
total qty(excl. electrodes) |  |  |  | total price
66 |  |  |  | 21.07

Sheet: Taul1
Component | Package | Source
ATMega328P | PDIP28 | Electronics club
10K resitor | 0603 | Johannes
0.1F capasitor | 1206 | Electronics club
hc-05 | custom | Johannes
Switch | custom | Electronics club | to be used during development
0 resistor | 0603 | Johannes
1K resitor | 0603 | Johannes
LED | 0603 | Johannes | BT indicator
Instrumentation amplifier TBD | DIP8 | Mouser/SP
LM324 | DIP14 | Mouser/SP
TL072IP | DIP8 | Mouser/SP
1N4148W-F | SMD | Mouser/SP | https://www.mouser.fi/ProductDetail/Diodes-Incorporated/1N4148W-7-F?qs=sGAEpiMZZMvilazpv%252bFqvbevgE8TPEOt
charge pump: MAX1720EUTG | SMD | Mouser | https://www.mouser.fi/ProductDetail/ON-Semiconductor/MAX1720EUTG
Electrodes | custom | https://www.medkit.fi/-1

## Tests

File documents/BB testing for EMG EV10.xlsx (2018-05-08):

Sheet: Taulukko1
Test num. | test name | PASS/FAIL/ONGOING | description
1 | supply voltages | PASS | no op amps or atmega attached
2 | Instrumental amplifier input/output | PASS | only inst. op amp attached
3 | LPF input/output | PASS | filter added
4 | HPF input/output | PASS | filter added
5 | 2nd op amp input/output | PASS | quad op amp added
6 | rectification input output | PASS
7 | 3rd op amp input output | PASS
8 | sign of life LED | PASS | atmega added
9 | ADC test | PASS
10 | BT test | PASS
 |  |  | problem | fix
 |  |  | hirveä melu HPF:n jälkeen | toinen LPF toiseeen oppariin = kytketään r14 rinnalle 10nF konkka -> fc =780Hz |  |  | x
 |  |  | Jos haluaa optimoida sykkeelle, pitää nostaa LPF rajataajuutta huomattavasti, oliko laskettu väärin? | r4 ja r5 82k -> 44k |  | uusi fc = 300Hz
 |  |  | toisen opparin vahvistu alentaa hitusen, jotta 10 mV ei laita kattoon | R14 150k -> 30k | G= -15 -> G= -3 |  | x
 |  |  | alenna viimeisen opparin vahvistusta? | tarkista vastukset r19 ja r20
 |  |  | järjestyksen vaihto? | ei toteuteta
 |  |  | vastuksia voitaisiin poistaa, myös yksi oppari myöhemmissä toteutuksissa

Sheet: 1
rail
+5V | OK | 5V in
-5V | OK
+3,3V | OK

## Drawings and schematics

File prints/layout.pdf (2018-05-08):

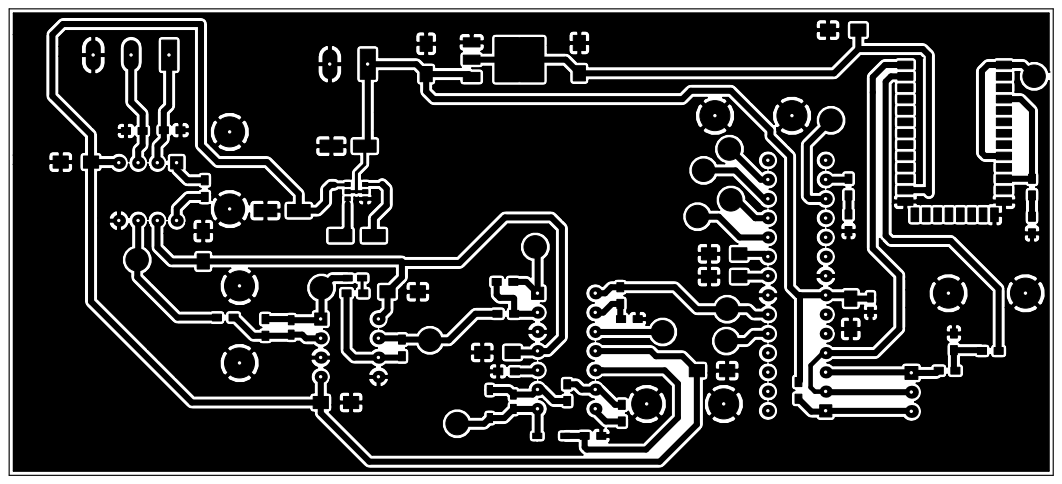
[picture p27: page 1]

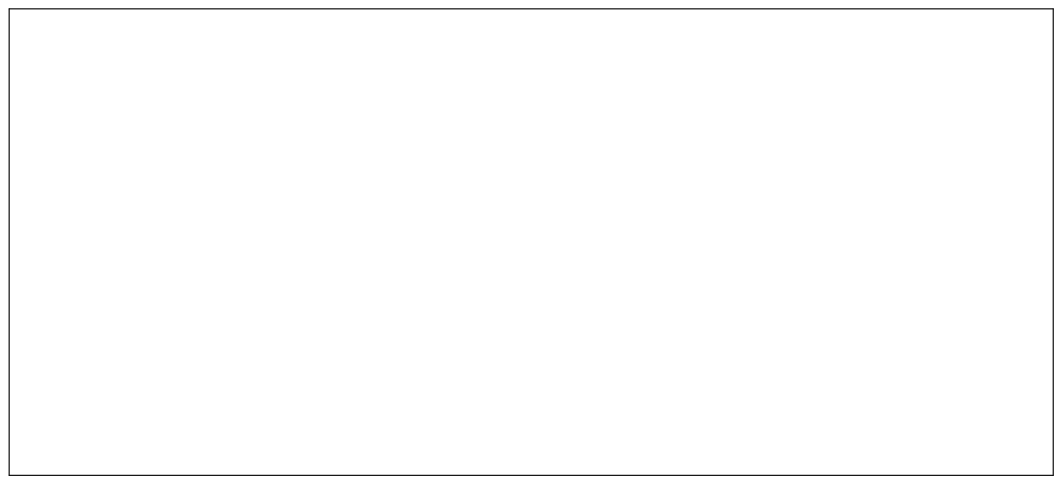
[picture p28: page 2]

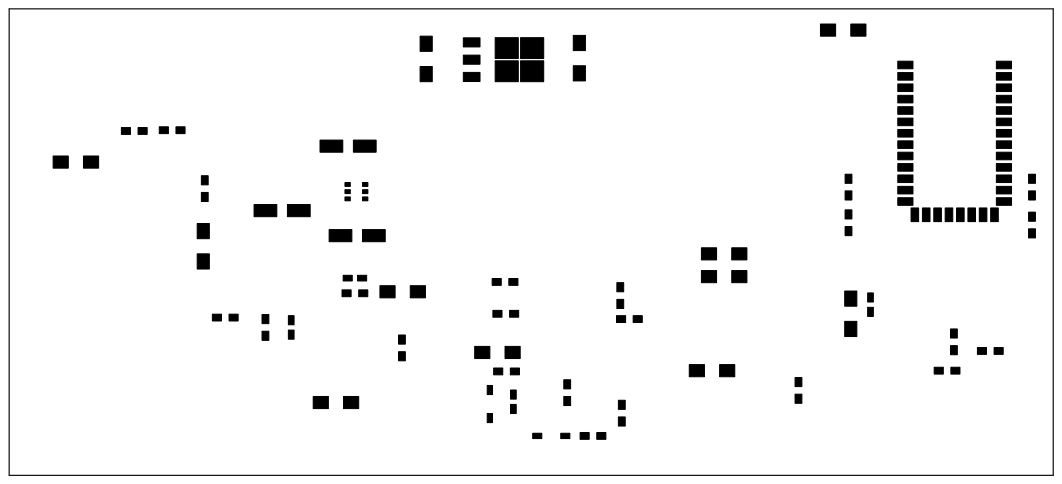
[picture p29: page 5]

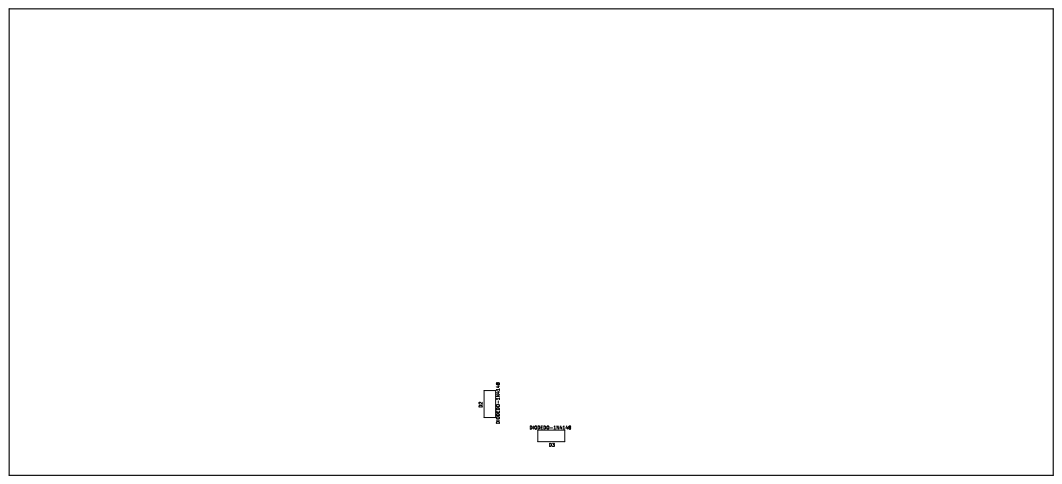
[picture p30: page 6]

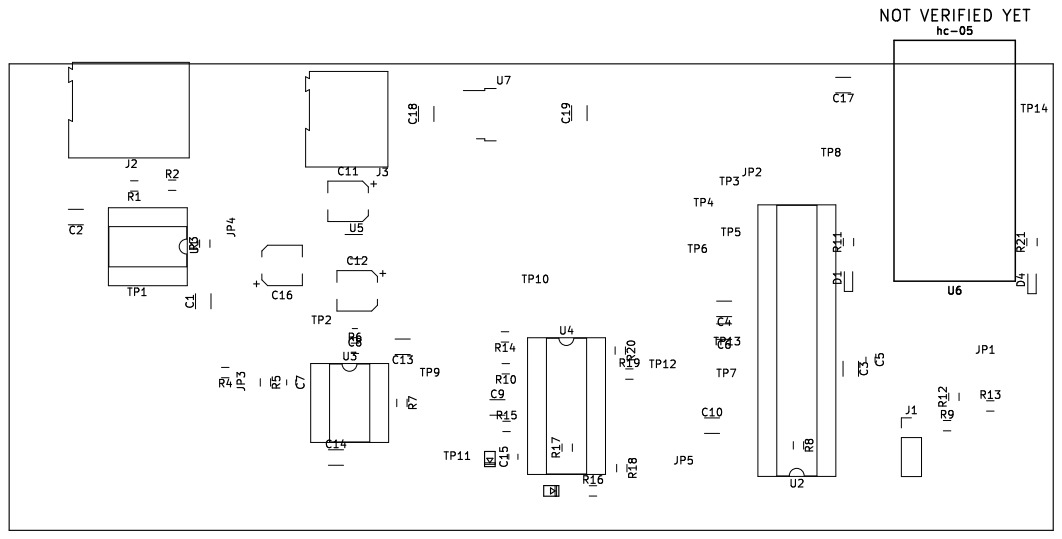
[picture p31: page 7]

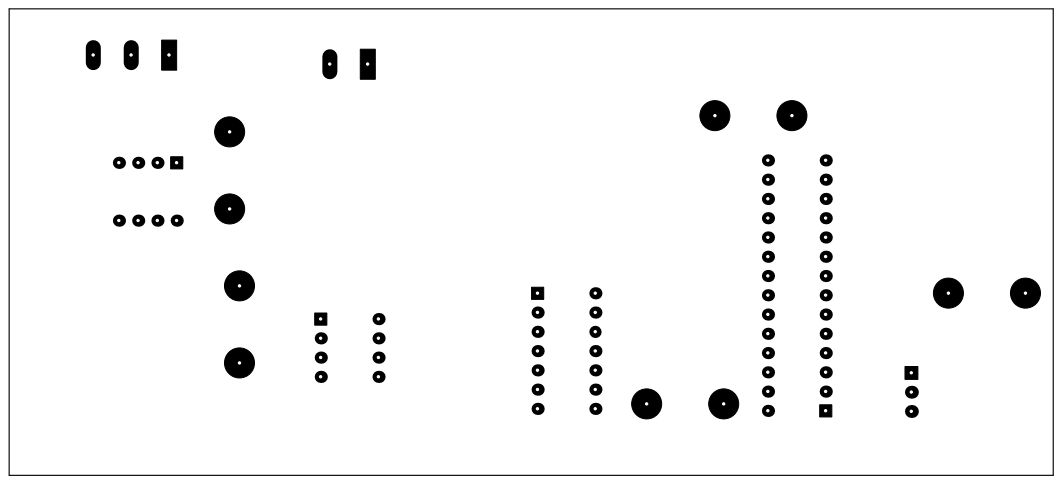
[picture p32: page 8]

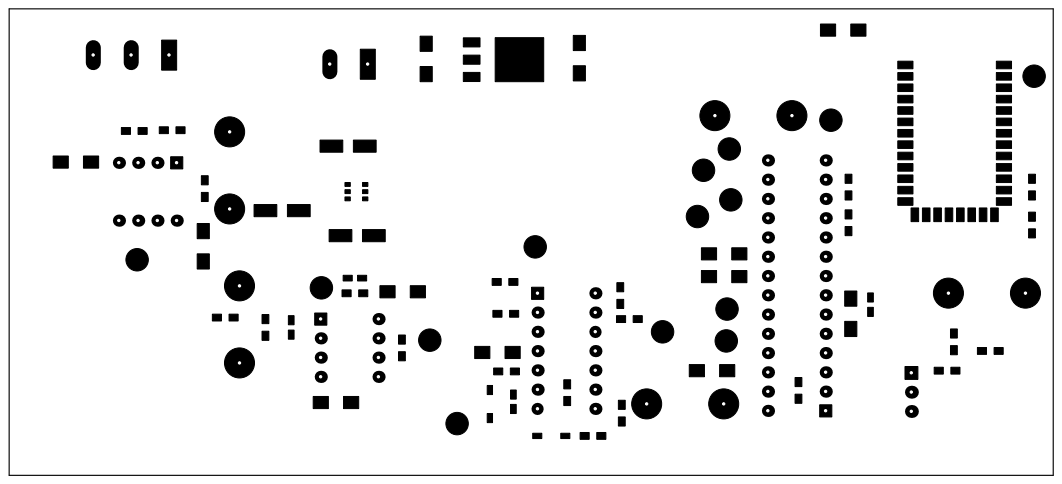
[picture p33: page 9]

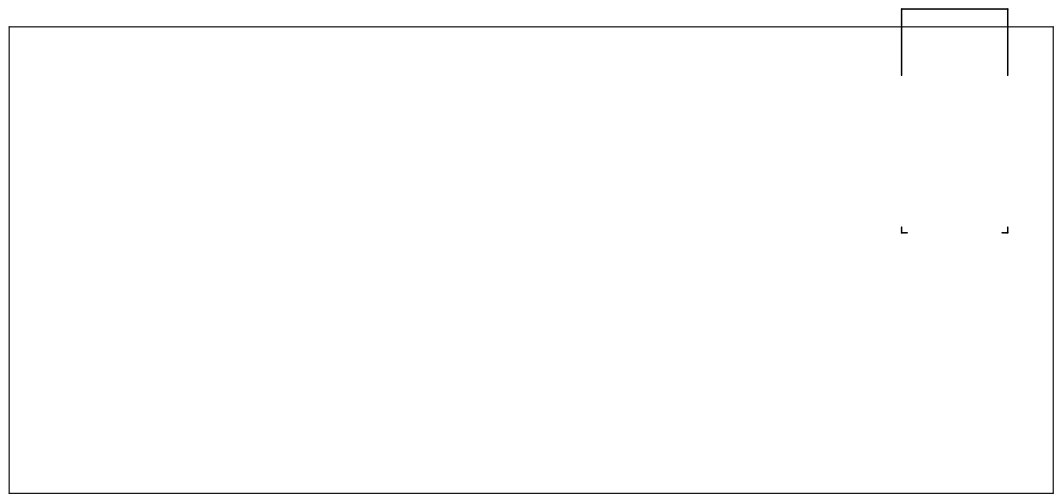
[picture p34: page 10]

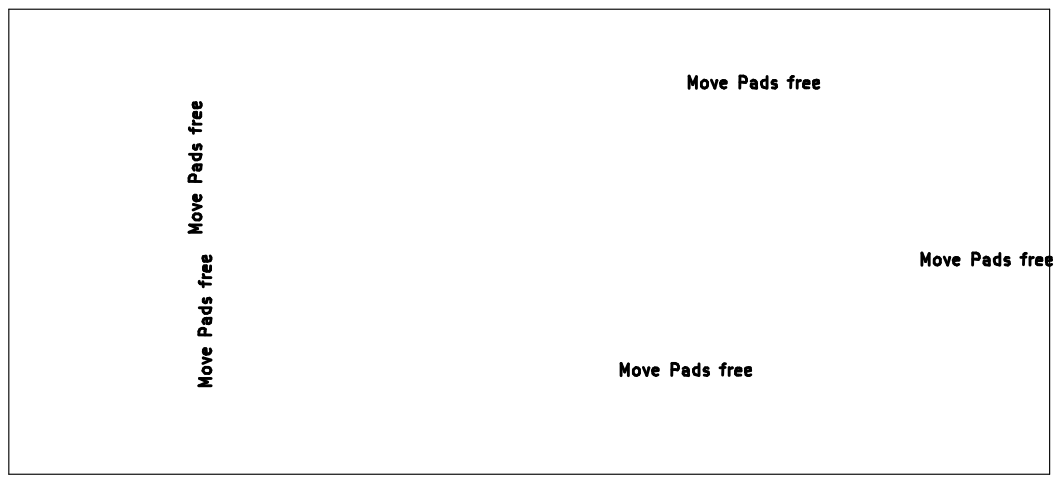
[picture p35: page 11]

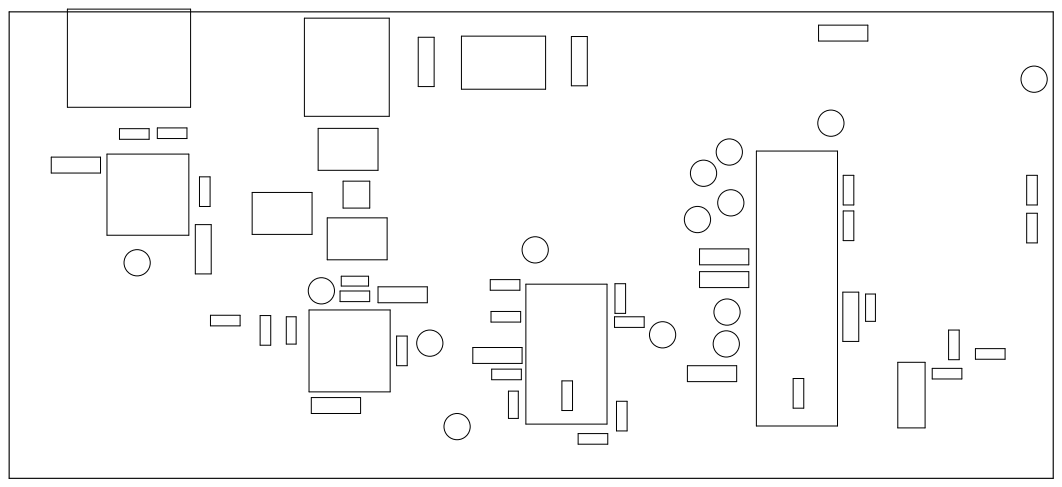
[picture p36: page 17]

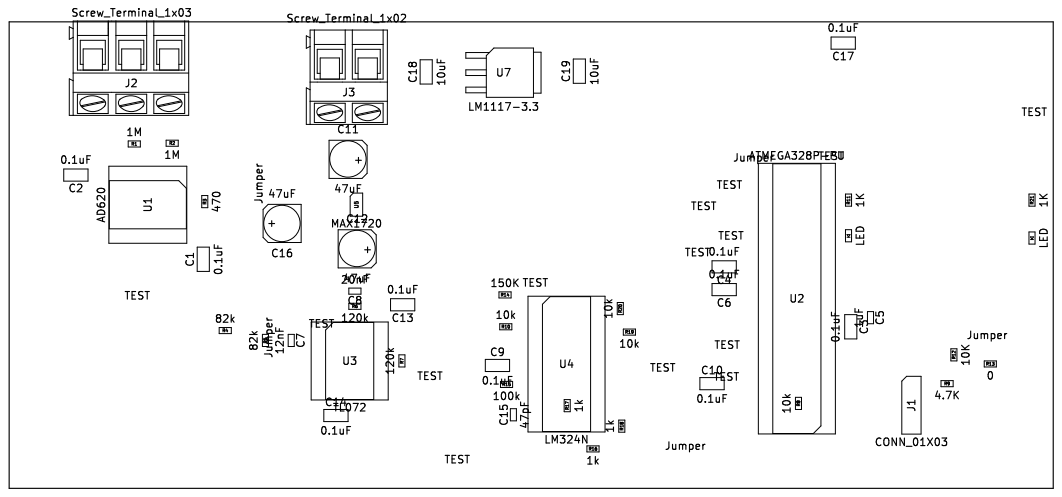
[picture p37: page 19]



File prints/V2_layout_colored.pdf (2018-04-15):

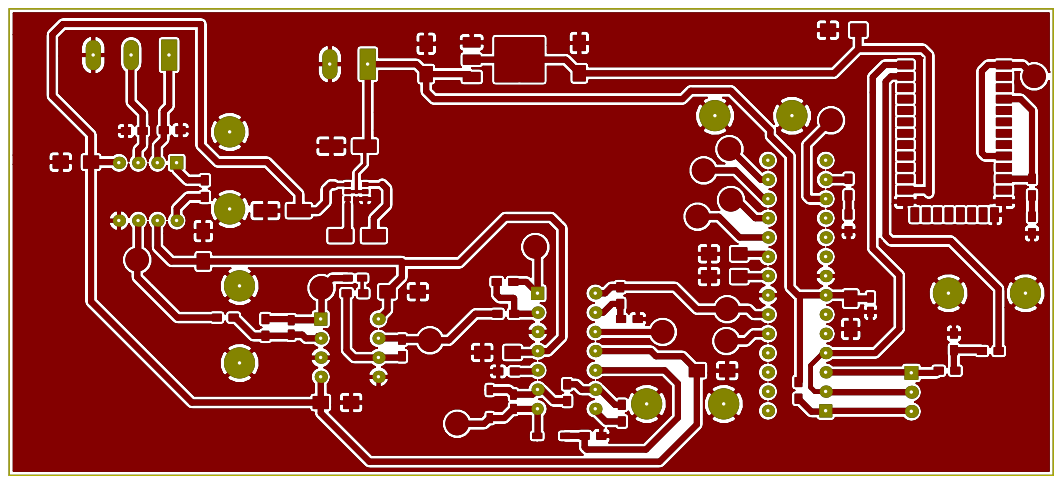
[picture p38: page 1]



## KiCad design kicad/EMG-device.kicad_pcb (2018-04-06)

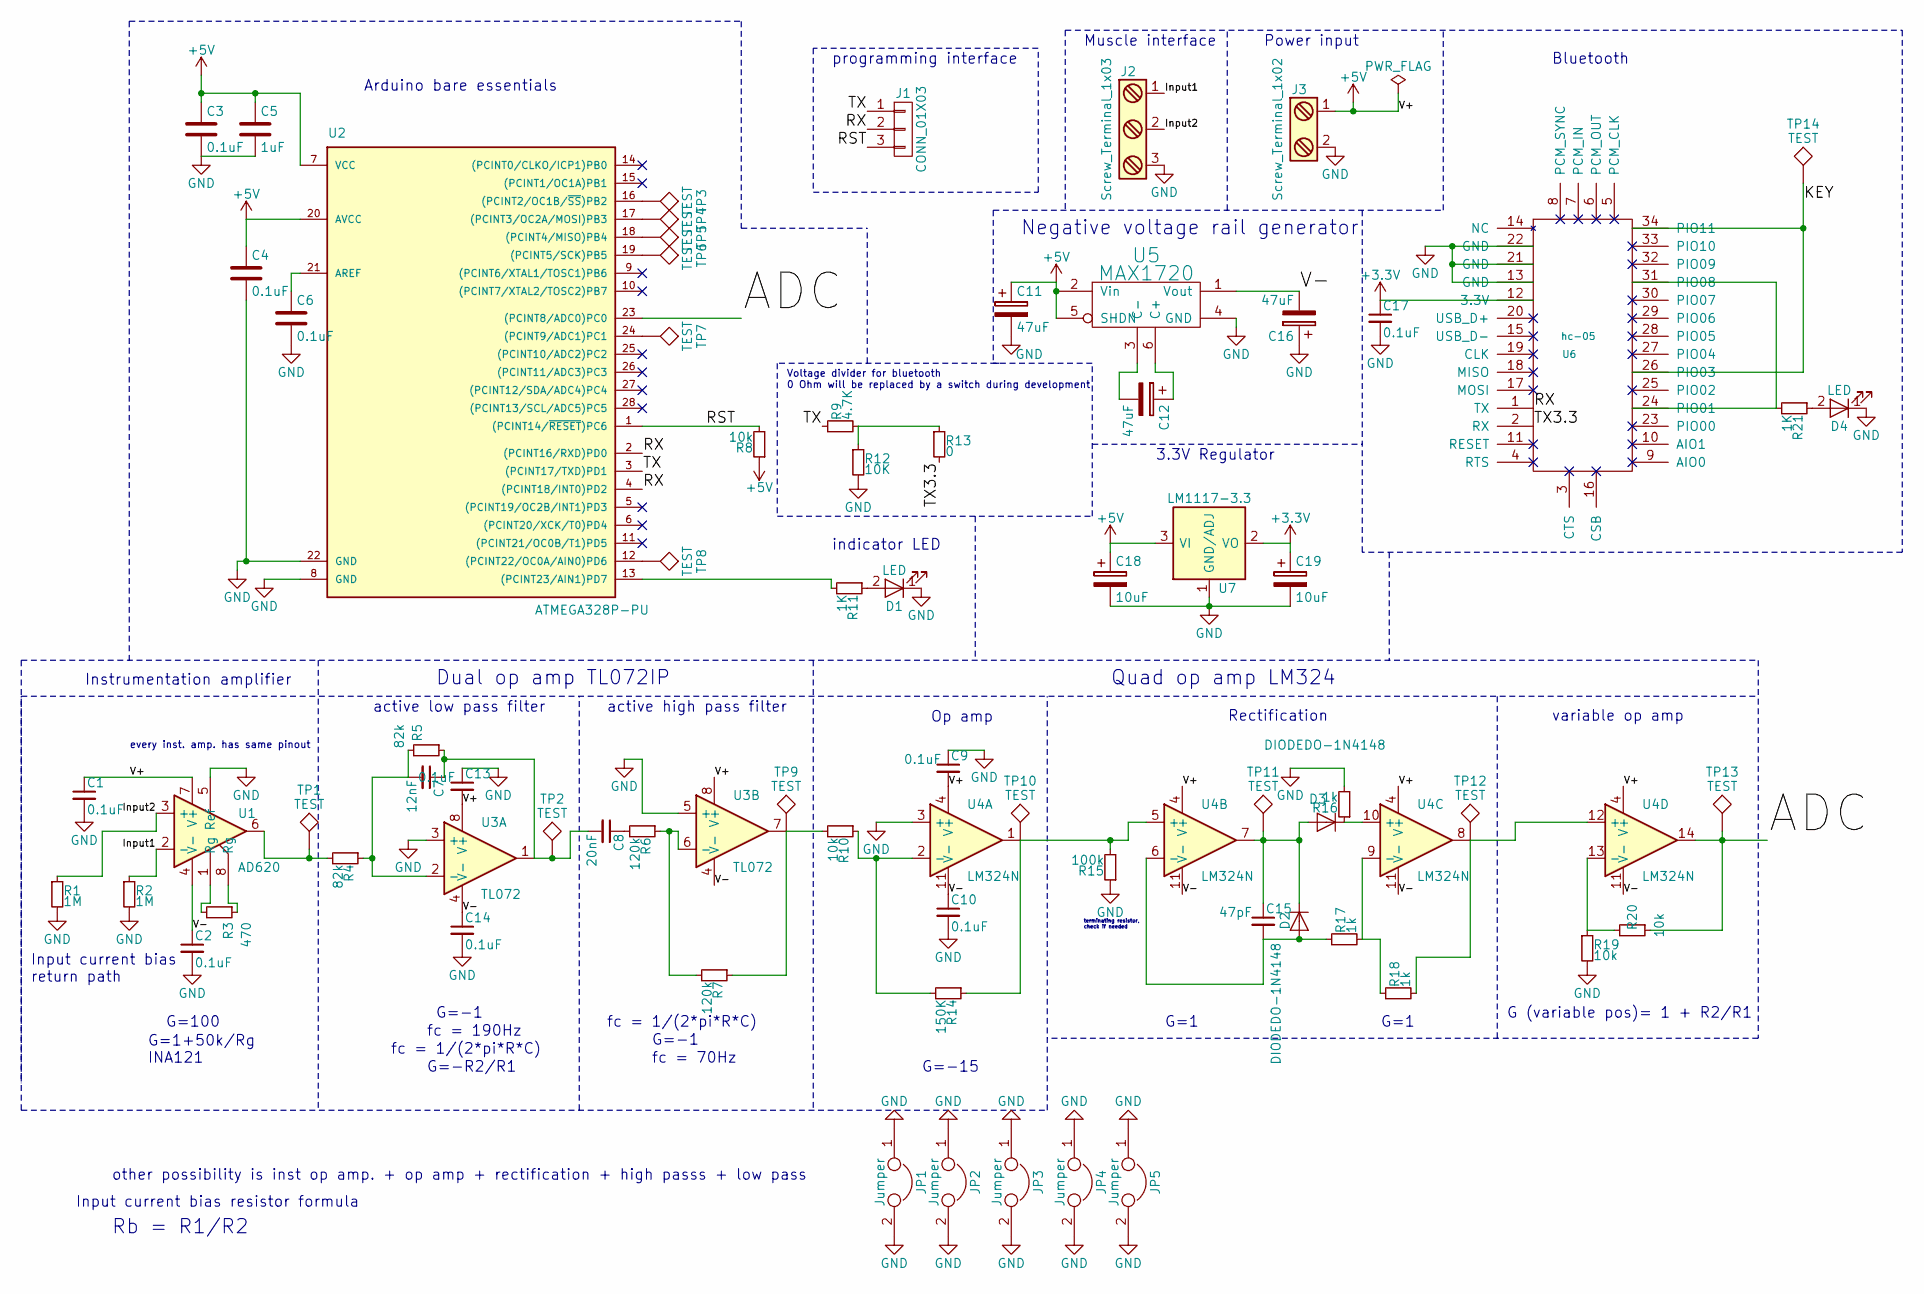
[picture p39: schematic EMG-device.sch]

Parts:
C1, C2, C3, C4, C6, C9, C10, C13, C14, C17: 0.1uF; C_1206_HandSoldering
C5: 1uF; C_0603_HandSoldering
C7: 12nF; C_0603_HandSoldering
C8: 20nF; C_0603_HandSoldering
C11, C12, C16: 47uF; CP_Elec_5x5.3
C15: 47pF; C_0603_HandSoldering
C18, C19: 10uF; CP_Tantalum_Case-U_EIA-6032-15_Hand
D1, D4: LED; LED_0603_HandSoldering
D2, D3: DIODEDO-1N4148; SOD-123
J1: CONN_01X03; Pin_Header_Straight_1x03_Pitch2.54mm
J2: Screw_Terminal_1x03; TerminalBlock_Altech_AK300-3_P5.00mm
J3: Screw_Terminal_1x02; TerminalBlock_Altech_AK300-2_P5.00mm
JP1, JP2, JP3, JP4: Jumper; WireConnection_2.00mmDrill
JP5: Jumper; SolderWirePad_2x_1mmDrill
R1, R2: 1M; R_0603_HandSoldering
R3: 470; R_0603_HandSoldering
R4, R5: 82k; R_0603_HandSoldering
R6, R7: 120k; R_0603_HandSoldering
R8, R10, R19, R20: 10k; R_0603_HandSoldering
R9: 4.7K; R_0603_HandSoldering
R11, R21: 1K; R_0603_HandSoldering
R12: 10K; R_0603_HandSoldering
R13: 0; R_0603_HandSoldering
R14: 150K; R_0603_HandSoldering
R15: 100k; R_0603_HandSoldering
R16, R17, R18: 1k; R_0603_HandSoldering
TP1, TP2, TP3, TP4, TP5, TP6, TP7, TP8, TP9, TP10, TP11, TP12, TP13, TP14: TEST; Measurement_Point_Round-SMD-Pad_Big
U1: AD620; DIP-8_W7.62mm_Socket
U2: ATMEGA328P-PU; DIP-28_W7.62mm_Socket
U3: TL072; DIP-8_W7.62mm_Socket
U4: LM324N; DIP-14_W7.62mm_Socket
U5: MAX1720; TSOP-6_1.65x3.05mm_Pitch0.95mm
U6: hc-05; HC-05
U7: LM1117-3.3; TO-252-3_TabPin2

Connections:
+3V3: C17.1, C19.1, U6.12 (3.3V), U7.2 (VO), U7.4 (VO)
+5V: C1.1, C3.1, C4.1, C5.1, C9.2, C11.1, C13.2, C18.1, J3.1, R8.1, U1.7 (V+), U2.7 (VCC), U2.20 (AVCC), U3.8 (V+), U4.4 (V+), U5.2 (Vin), U5.5 (SHDN), U7.3 (VI)
/ADC: R20.1, TP13.1, U2.23 ((PCINT8/ADC0)PC0), U4.14
/Input1: J2.1, R2.1, U1.2 (-)
/Input2: J2.2, R1.1, U1.3 (+)
/KEY: TP14.1, U6.26 (PIO03), U6.34 (PIO11)
/RST: J1.3, R8.2, U2.1 ((PCINT14/~RESET~)PC6)
/RX: J1.2, U2.2 ((PCINT16/RXD)PD0), U2.4 ((PCINT18/INT0)PD2), U6.1 (TX)
/TX: J1.1, R9.1, U2.3 ((PCINT17/TXD)PD1)
/TX3.3: R13.2, U6.2 (RX)
/V-: C2.1, C10.1, C14.1, C16.2, U1.4 (V-), U3.4 (V-), U4.11 (V-), U5.1 (Vout)
GND: C1.2, C2.2, C3.2, C4.2, C5.2, C6.2, C9.1, C10.2, C11.2, C13.1, C14.2, C16.1, C17.2, C18.2, C19.2, D1.1 (K), D4.1 (K), J2.3, J3.2, JP1.1, JP1.2, JP2.1, JP2.2, JP3.1, JP3.2, JP4.1, JP4.2, JP5.1, JP5.2, R1.2, R2.2, R12.2, R15.1, R16.2, R19.2, U1.5 (Ref), U2.8 (GND), U2.22 (GND), U3.3 (+), U3.5 (+), U4.3 (+), U5.4 (GND), U6.13 (GND), U6.21 (GND), U6.22 (GND), U7.1 (GND/ADJ)
unnamed: C6.1, U2.21 (AREF)
unnamed: C7.1, C8.2, R5.1, TP2.1, U3.1
unnamed: C7.2, R4.1, R5.2, U3.2 (-)
unnamed: C8.1, R6.2
unnamed: C12.1, U5.6 (C+)
unnamed: C12.2, U5.3 (C-)
unnamed: C15.1, D2.C, D3.A, TP11.1, U4.7
unnamed: C15.2, D2.A, R17.1, U4.6 (-)
unnamed: D1.2 (A), R11.1
unnamed: D3.C, R16.1, U4.10 (+)
unnamed: D4.2 (A), R21.1
unnamed: R3.1, U1.8 (Rg)
unnamed: R3.2, U1.1 (Rg)
unnamed: R4.2, TP1.1, U1.6
unnamed: R6.1, R7.2, U3.6 (-)
unnamed: R10.1, R14.2, U4.2 (-)
unnamed: R7.1, R10.2, TP9.1, U3.7
unnamed: R11.2, U2.13 ((PCINT23/AIN1)PD7)
unnamed: R9.2, R12.1, R13.1
unnamed: R14.1, R15.2, TP10.1, U4.1, U4.5 (+)
unnamed: R17.2, R18.1, U4.9 (-)
unnamed: R18.2, TP12.1, U4.8, U4.12 (+)
unnamed: R19.1, R20.2, U4.13 (-)
unnamed: R21.2, U6.24 (PIO01), U6.31 (PIO08)
unnamed: TP3.1, U2.16 ((PCINT2/OC1B/~SS~)PB2)
unnamed: TP4.1, U2.17 ((PCINT3/OC2A/MOSI)PB3)
unnamed: TP5.1, U2.18 ((PCINT4/MISO)PB4)
unnamed: TP6.1, U2.19 ((PCINT5/SCK)PB5)
unnamed: TP7.1, U2.24 ((PCINT9/ADC1)PC1)
unnamed: TP8.1, U2.12 ((PCINT22/OC0A/AIN0)PD6)

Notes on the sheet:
Arduino bare essentials
programming interface
Bluetooth
Voltage divider for bluetooth 0 Ohm will be replaced by a switch during development
indicator LED
Instrumentation amplifier
every inst. amp. has same pinout
Muscle interface
Op amp
active high pass filter
Quad op amp LM324
Rectification
active low pass filter
Dual op amp TL072IP
variable op amp
terminating resistor, check if needed
Power input
Negative voltage rail generator
Rb = R1/R2
Input current bias return path
fc = 1/(2*pi*R*C)
G=-1
fc = 70Hz
G=100
G=-15
G=1
G=-1
fc = 190Hz
other possibility is inst op amp. + op amp + rectification + high passs + low pass
G (variable pos)= 1 + R2/R1
Input current bias resistor formula
G=1+50k/Rg INA121
G=-R2/R1
3.3V Regulator

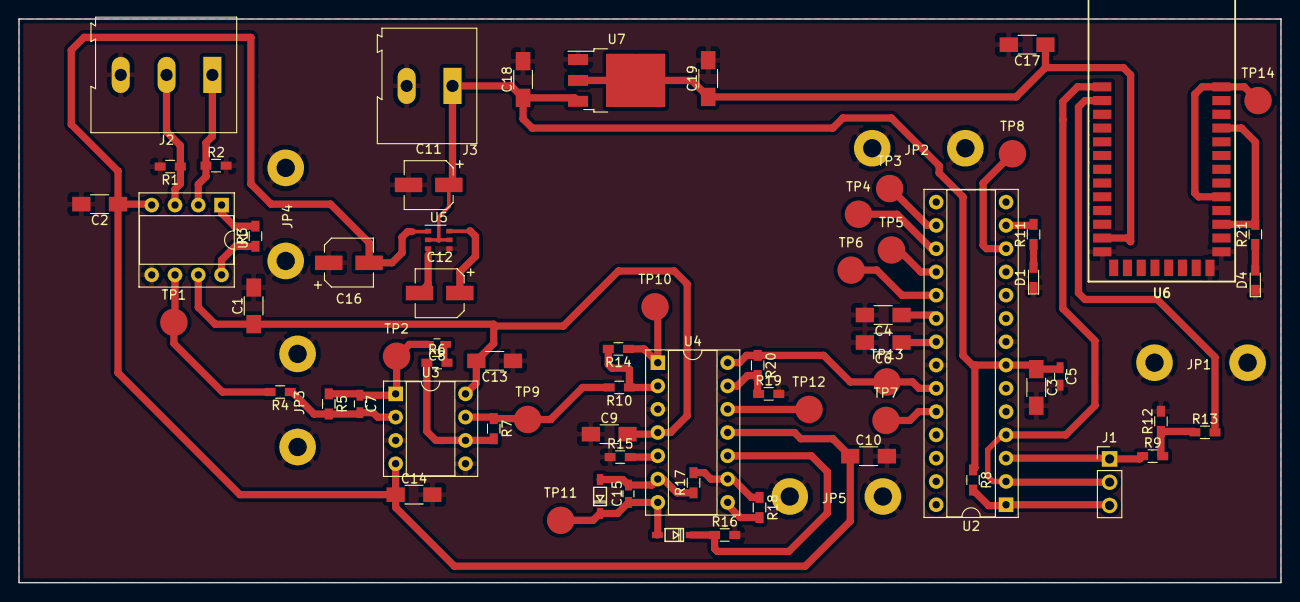
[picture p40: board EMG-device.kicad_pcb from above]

Board: 2 copper layers, 137.7 x 61.5 mm, 73 parts (0 on the bottom side), 42 nets.

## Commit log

2018-03-30 files created
    files created
    [EMG_BOM.xlsx]
2018-03-30 Moved files, schematic V1 done
    [EMG-device.kicad_pcb, EMG-device.sch, EMG_BOM.xlsx, elekerhon komponentit.xlsx]
2018-03-31 input bias resistor document
2018-03-31 schematics done
    schematics 1.0 done
    BOM updated, but not ready
    [EMG-device.sch, EMG_BOM.xlsx]
2018-04-02 BOM done, added missing components to schematics, added footpints
    [EMG-device.sch, EMG_BOM.xlsx]
2018-04-02 layout done, some changes in schematics
    [EMG-device.sch]
2018-04-04 wires xhanged to 0.8mil
    [EMG-device.kicad_pcb]
2018-04-06 layout wires increased in size
    [EMG-device.kicad_pcb]
2018-05-08 final adjustments
    [EMG_BOM.xlsx, EMG_BOM_soldered_components.xlsx]
2018-05-08 Mechanics added
    [BB testing for EMG EV10.xlsx, mittari.blend]
